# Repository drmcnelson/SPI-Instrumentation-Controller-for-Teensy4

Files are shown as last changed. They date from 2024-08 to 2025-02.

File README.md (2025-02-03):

# SPI Instrumentation Controller using Teensy 4.0

<p align="center">
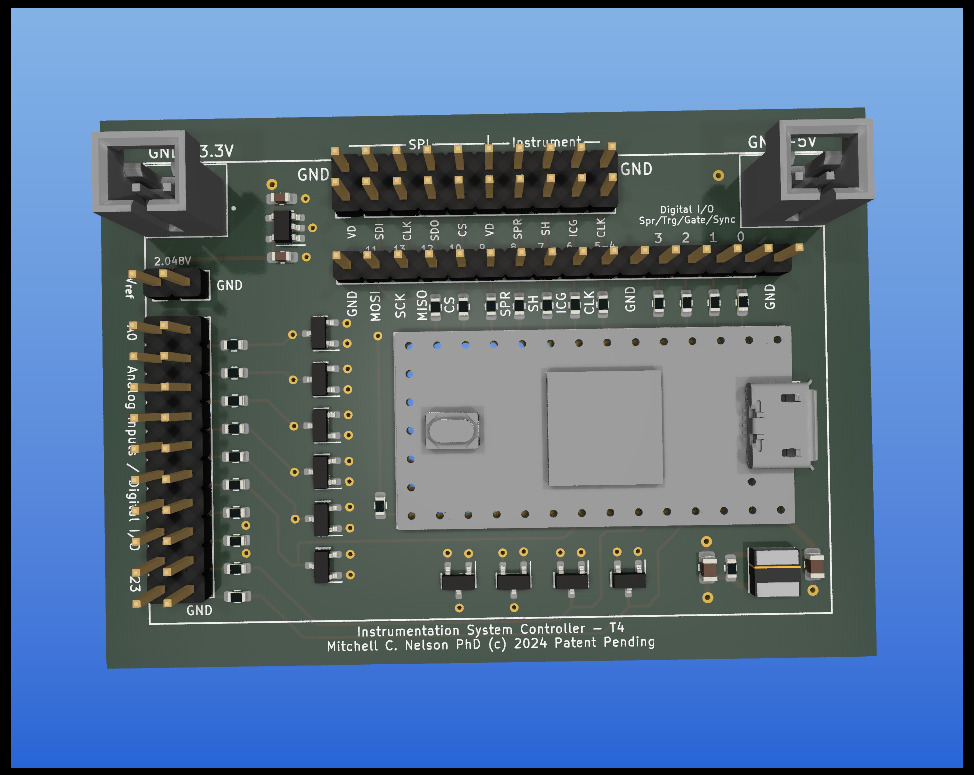
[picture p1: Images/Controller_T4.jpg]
Controller_T4

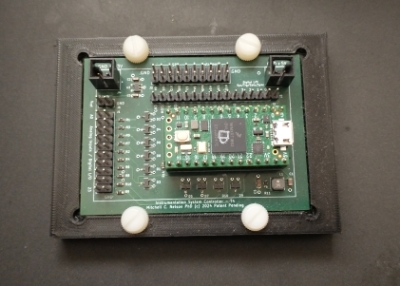
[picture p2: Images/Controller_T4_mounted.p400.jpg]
Controller_T4

</p>

Controller board for the SPI Instrumentation project, hosts a Teensy 4.0 and provides connectors for SPI, instrumentation control, 3.3V and 5V power, a precision voltage references, dedicated pins for trigger and gate input, sync and busy output and a set of pins that can be used for analog input or digital i/o.   The connectors are identified in images below.

## Connectors

The following shows the location of the pins for the SPI interface circled in red.

<p align="center">
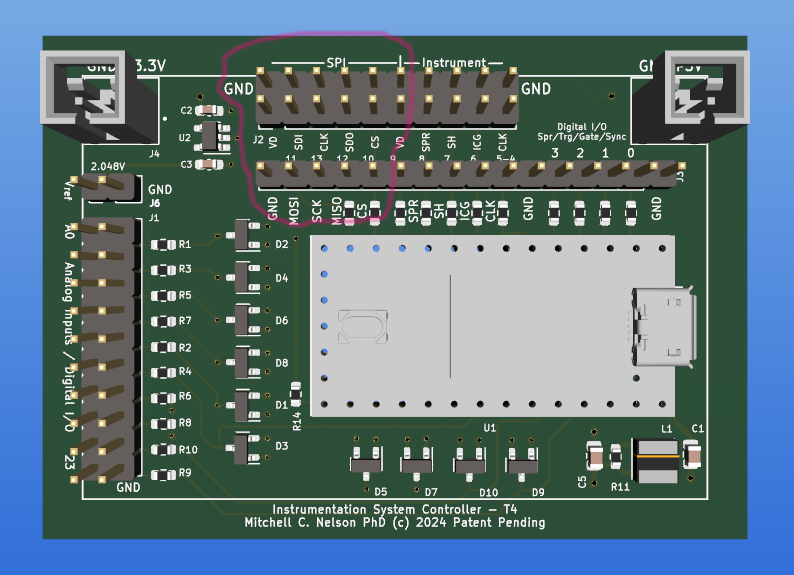
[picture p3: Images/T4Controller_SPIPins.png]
Controller_T4_SPI

</p>

The following shows the location of the pins for interfacing to the Linear CCD SPI boards, circled in red.

<p align="center">
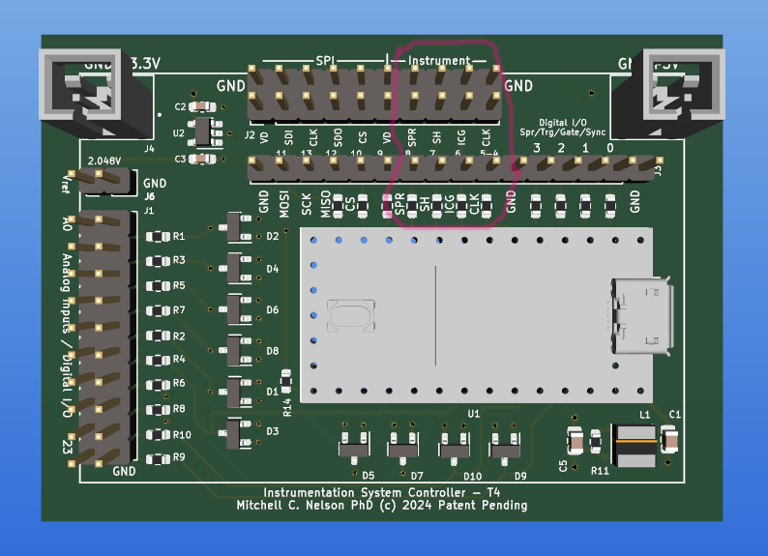
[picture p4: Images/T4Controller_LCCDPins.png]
Controller_T4_LCCD

</p>

The following shows the location of the pins for trigger and gate input and sync and busy output, circled in red.

<p align="center">
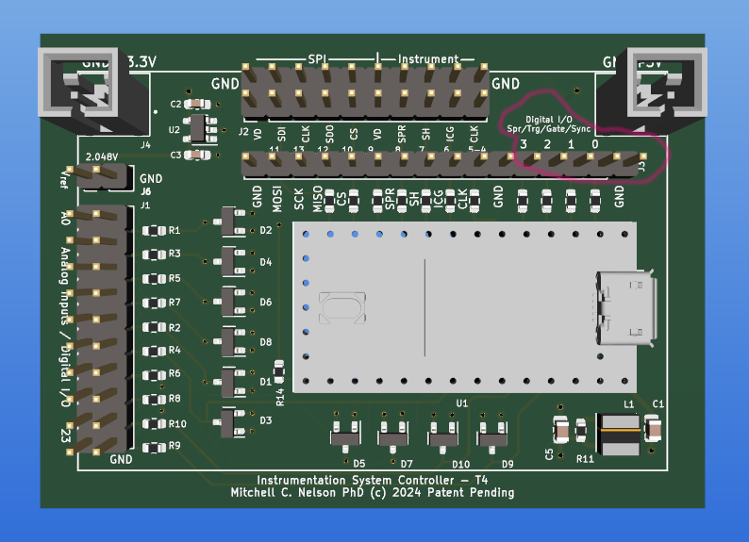
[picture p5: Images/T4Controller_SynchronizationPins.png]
Controller_T4_LCCD

</p>

## Example use
Here is an example of how the board is used, the other two boards in this picture are the InAmp and +5V,-5V power supply.

<p align="center">
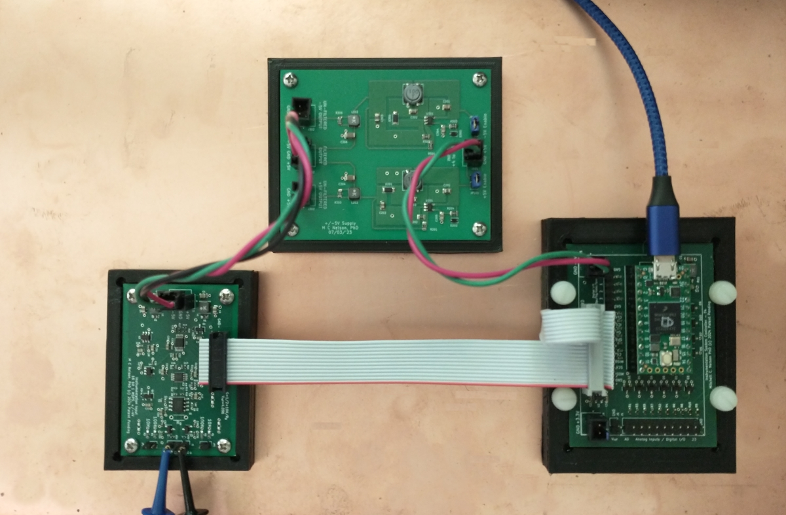
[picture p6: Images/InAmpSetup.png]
Controller_setup

</p>

## Obtaining boards

This repo includes files for FAB and assembly. 

You can [order assembled boards from PCBWAY here](https://www.pcbway.com/project/shareproject/Controller_Teensy_4_0_for_SPI_Instrumentation_boards_4b27edb1.html).

To assemble the board yourself you will need a reflow oven.  You can order bare boards from a sevice such as PCBWay or AllPCB, and use the BOM spreadsheet file to order parts from Digikey

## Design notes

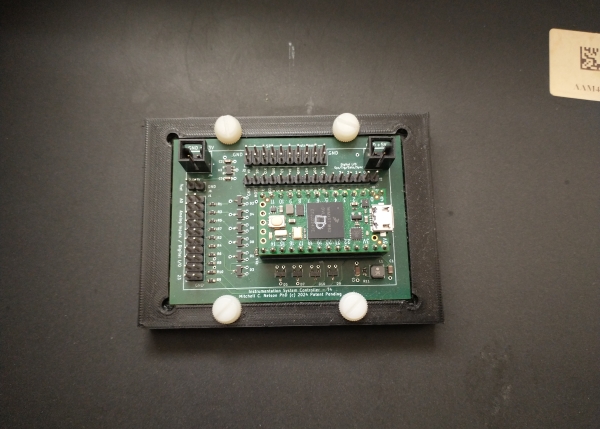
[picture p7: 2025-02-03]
Images/Controller_T4_mounted.jpg

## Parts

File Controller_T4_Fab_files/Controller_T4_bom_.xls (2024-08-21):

SMT Components | References | Value | Description | Footprint | Quantity Per PCB | Digikey
1 | C1 C5 | 22uF | CAP CER 22UF 25V X5R | C_0805_2012Metric | 2 | 490-12389-1-ND
2 | C2 | 10uF | Cap Cer 10uf 16V X5R | C_0603_1608Metric | 1 | 490-12317-1-ND
3 | C3 | 1uF | Cap Cer 1uf 16V X5R | C_0603_1608Metric | 1 | 1276-1034-1-ND
4 | D1-D10 | BAV99 | DIODE ARR GP 100V 215MA TO236AB | SOT-23 | 10 | 1727-2914-1-ND
5 | L1 | 10uH | FIXED IND 10UH 1.2A 180 MOHM SMD | L_Taiyo-Yuden_NR-40xx | 1 | 587-2886-1-ND
6 | R12-R23 | 49.9 | RES 49.9 OHM 1% 1/10W 0603 | R_0603_1608Metric | 12 | RMCF0603FT49R9CT-ND
7 | R1-R11 | 100R | RES 100 OHM 1% 1/4W 0603 | R_0603_1608Metric | 11 | 10-ERJ-UP3F1000VCT-ND
8 | U2 | LM4132xMF-2.0 | Fixed Ref 2.048V in SOT-23-5 | Package_TO_SOT_SMD:SOT-23-5 | 1 | LM4132BMF-2.0/NOPBCT-ND
 |  |  |  | Total SMT components | 39
Thru-Hole Parts
9 | J4-J5 |  | CONN HEADER VERT 2POS 2.54MM | MOLEX_705430001 | 2 | WM4800-ND
10 | J6 |  | CONN HEADER VERT 2POS 2.54MM | PinHeader_1x02_P2.54mm_Vertical | 1 | 3M156268-02-ND
11 | J3 | Conn_01x16_Male | CONN HEADER VERT 16POS 2.54MM | PinHeader_1x16_P2.54mm_Vertical | 1 | 3M156268-16-ND
12 | J1-J2 | Conn_02x10_Odd_Even | CONN HEADER VERT 20POS 2.54MM | PinHeader_2x10_P2.54mm_Vertical | 2 | 3M156308-20-ND
 |  |  |  | Total Thru-hole Components | 6
Teensy 4.0
DNP | Teensy (U1) | Teensy4.0 | Teensy4.0 | Teensy40 (2rows 0.6”, 14pins 0.1”, aligns with dip 28 W15.24) | 1 | 1568-DEV-16997-ND
DNP | Headers (U1) |  | Thru hole Headers, as socket for the Teensy4 |  | 2 | S7047-ND
DNP | Pins (U1) |  | Mating pins for the headers |  | 2 | 929647-01-14-EU
Accessories
DNP |  |  | Ribbon Cable |  | 1 | 3M157973-1-ND
DNP |  |  | Ribbon Cable IDC Free Hanging End |  | 2 | MKC20A-ND
DNP |  |  | Mating 2-pin connector |  | 2 | WM2900-ND
DNP |  |  | Crimp Pins 22-24awg, gold |  | 4 | WM2512-ND

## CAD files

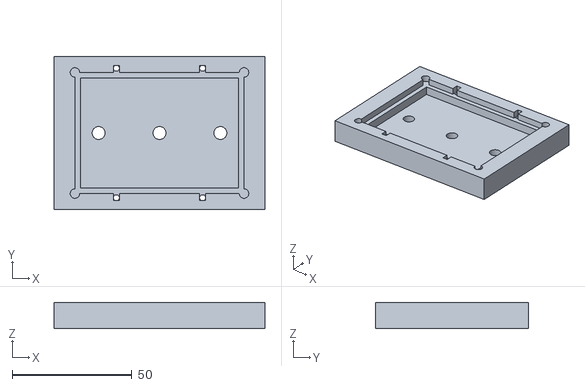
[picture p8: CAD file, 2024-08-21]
Base_3D_Printer_files/Controller_T4_base-Controller_T4_base.stl
88.0 x 64.0 x 11.0

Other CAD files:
Base_3D_Printer_files/Controller_T4_base.FCStd

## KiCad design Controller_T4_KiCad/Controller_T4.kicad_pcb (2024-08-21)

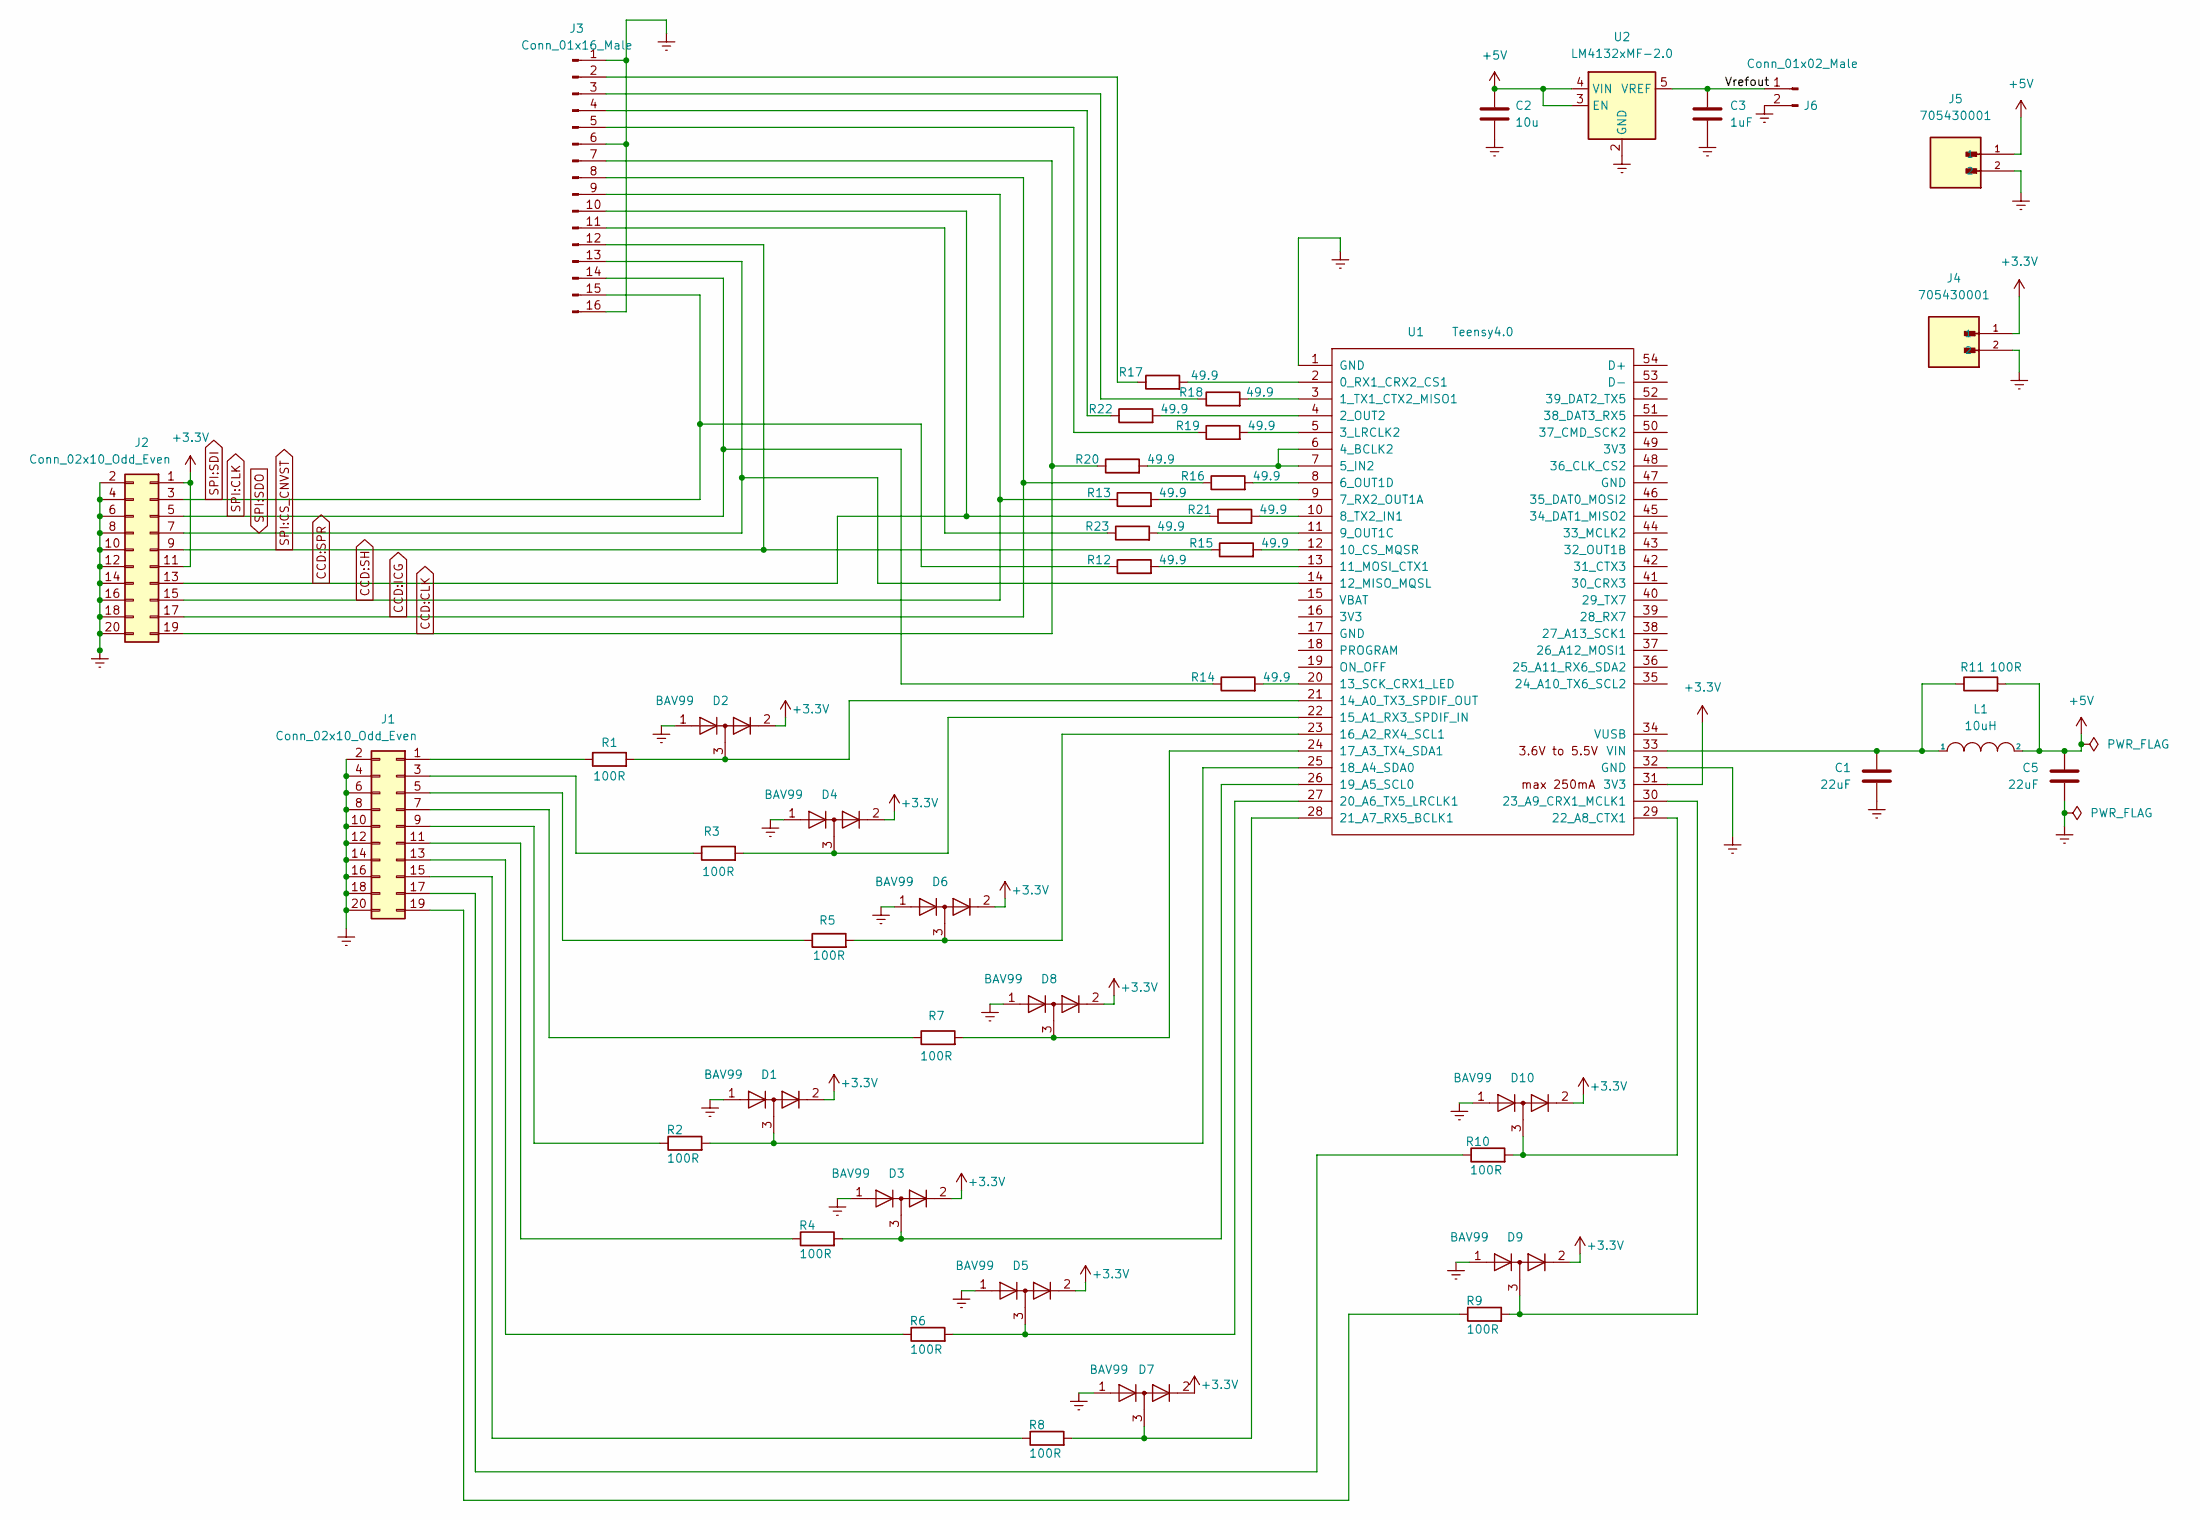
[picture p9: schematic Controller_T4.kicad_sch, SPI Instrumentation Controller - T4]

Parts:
C1, C5: 22uF; C_0805_2012Metric; Digikey 490-12389-1-ND
C2: 10u; C_0603_1608Metric_Pad1.08x0.95mm_HandSolder; Digikey 490-12317-1-ND
C3: 1uF; C_0603_1608Metric_Pad1.08x0.95mm_HandSolder; Digikey 1276-1034-1-ND
D1, D2, D3, D4, D5, D6, D7, D8, D9, D10: BAV99; SOT-23; Digikey 1727-2914-1-ND
J1, J2: Conn_02x10_Odd_Even; PinHeader_2x10_P2.54mm_Vertical; Digikey 3M156308-20-ND
J3: Conn_01x16_Male; PinHeader_1x16_P2.54mm_Vertical; Digikey 3M156268-16-ND
J4, J5: 705430001; MOLEX_705430001; PARTREV M1; Digikey WM4800-ND
J6: Conn_01x02_Male; PinHeader_1x02_P2.54mm_Vertical; Digikey 3M156268-02-ND
L1: 10uH; L_Taiyo-Yuden_NR-40xx; Digikey 587-2886-1-ND
R1, R2, R3, R4, R5, R6, R7, R8, R9, R10, R11: 100R; R_0603_1608Metric; Digikey 10-ERJ-UP3F1000VCT-ND
R12, R13, R14, R15, R16, R17, R18, R19, R20, R21, R22, R23: 49.9; R_0603_1608Metric; Digikey RMCF0603FT49R9CT-ND
U1: Teensy4.0; Teensy40; Digikey 1568-DEV-16997-ND
U2: LM4132xMF-2.0; SOT-23-5; Digikey LM4132BMF-2.0/NOPBCT-ND

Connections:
+3.3V: D1.2 (A), D2.2 (A), D3.2 (A), D4.2 (A), D5.2 (A), D6.2 (A), D7.2 (A), D8.2 (A), D9.2 (A), D10.2 (A), J2.1, J2.11, J4.1, U1.31 (3V3)
+5V: C2.1, C5.1, J5.1, L1.2, R11.2, U2.3 (EN), U2.4 (VIN)
/Vrefout: C3.1, J6.1, U2.5 (VREF)
CCD:CLK: J2.19, J3.7, R20.1
CCD:ICG: J2.17, J3.8, R16.1
CCD:SH: J2.15, J3.9, R13.1
CCD:SPR: J2.13, J3.10, R21.1
Earth: C1.2, C2.2, C3.2, C5.2, D1.1 (K), D2.1 (K), D3.1 (K), D4.1 (K), D5.1 (K), D6.1 (K), D7.1 (K), D8.1 (K), D9.1 (K), D10.1 (K), J1.2, J1.4, J1.6, J1.8, J1.10, J1.12, J1.14, J1.16, J1.18, J1.20, J2.2, J2.4, J2.6, J2.8, J2.10, J2.12, J2.14, J2.16, J2.18, J2.20, J3.1, J3.6, J3.16, J4.2, J5.2, J6.2, U1.1 (GND), U1.32 (GND), U2.2 (GND)
unnamed: C1.1, L1.1, R11.1, U1.33 (VIN)
unnamed: D1.3 (K), R2.2, U1.25 (18_A4_SDA0)
unnamed: D2.3 (K), R1.2, U1.21 (14_A0_TX3_SPDIF_OUT)
unnamed: D3.3 (K), R4.2, U1.26 (19_A5_SCL0)
unnamed: D4.3 (K), R3.2, U1.22 (15_A1_RX3_SPDIF_IN)
unnamed: D5.3 (K), R6.2, U1.27 (20_A6_TX5_LRCLK1)
unnamed: D6.3 (K), R5.2, U1.23 (16_A2_RX4_SCL1)
unnamed: D7.3 (K), R8.2, U1.28 (21_A7_RX5_BCLK1)
unnamed: D8.3 (K), R7.2, U1.24 (17_A3_TX4_SDA1)
unnamed: D9.3 (K), R9.2, U1.30 (23_A9_CRX1_MCLK1)
unnamed: D10.3 (K), R10.2, U1.29 (22_A8_CTX1)
unnamed: J1.1, R1.1
unnamed: J1.3, R3.1
unnamed: J1.5, R5.1
unnamed: J1.7, R7.1
unnamed: J1.9, R2.1
unnamed: J1.11, R4.1
unnamed: J1.13, R6.1
unnamed: J1.15, R8.1
unnamed: J1.17, R10.1
unnamed: J1.19, R9.1
unnamed: J3.2, R17.1
unnamed: J3.3, R18.1
unnamed: J3.4, R22.1
unnamed: J3.5, R19.1
unnamed: J3.11, R23.1
unnamed: R12.2, U1.13 (11_MOSI_CTX1)
unnamed: R13.2, U1.9 (7_RX2_OUT1A)
unnamed: R14.2, U1.20 (13_SCK_CRX1_LED)
unnamed: R15.2, U1.12 (10_CS_MQSR)
unnamed: R16.2, U1.8 (6_OUT1D)
unnamed: R17.2, U1.2 (0_RX1_CRX2_CS1)
unnamed: R18.2, U1.3 (1_TX1_CTX2_MISO1)
unnamed: R19.2, U1.5 (3_LRCLK2)
unnamed: R20.2, U1.6 (4_BCLK2), U1.7 (5_IN2)
unnamed: R21.2, U1.10 (8_TX2_IN1)
unnamed: R22.2, U1.4 (2_OUT2)
unnamed: R23.2, U1.11 (9_OUT1C)
SPI:CLK: J2.5, J3.14, R14.1
SPI:CS_CNVST: J2.9, J3.12, R15.1
SPI:SDI: J2.3, J3.15, R12.1
SPI:SDO: J2.7, J3.13, U1.14 (12_MISO_MQSL)

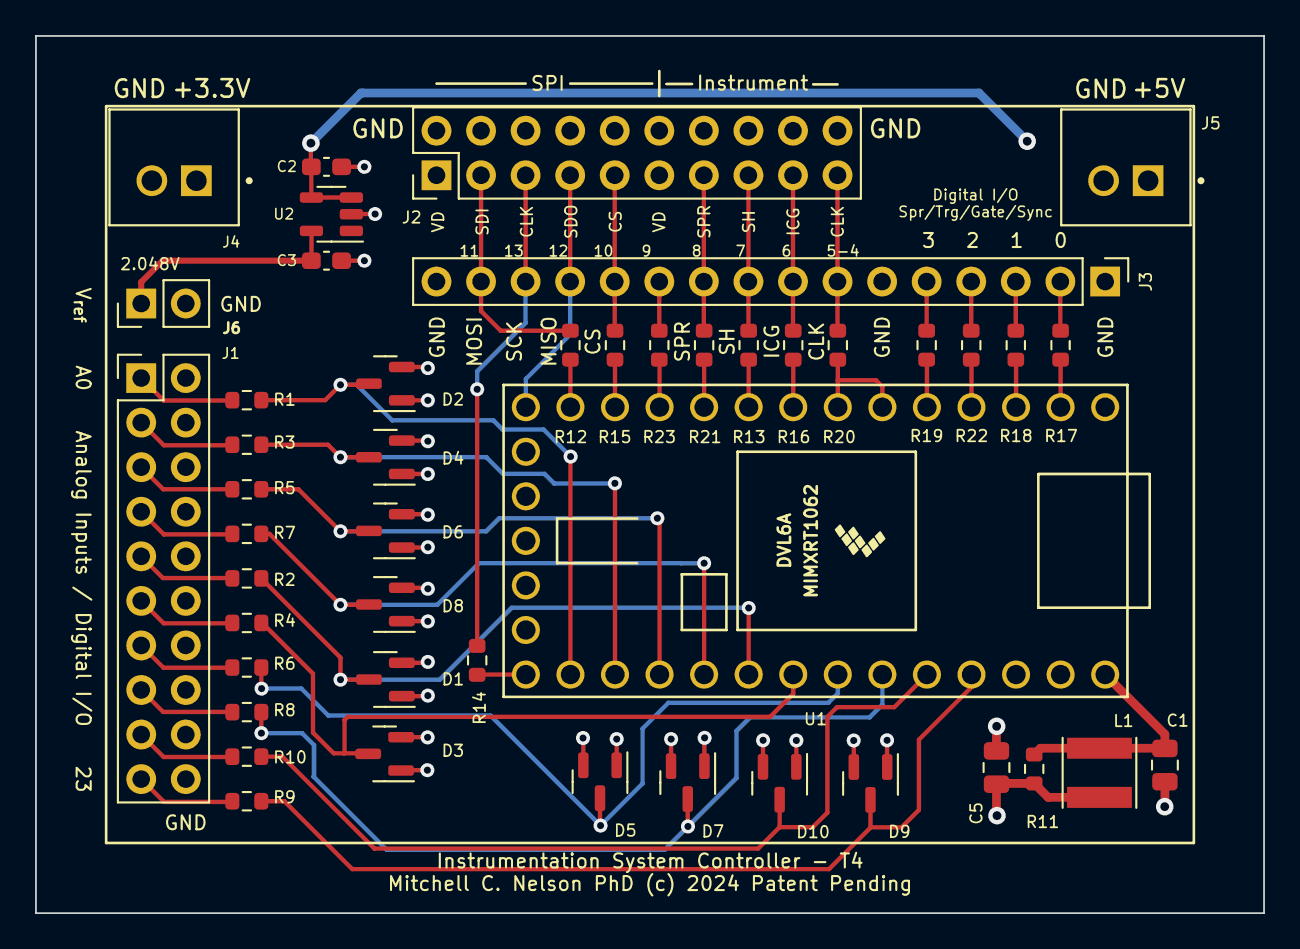
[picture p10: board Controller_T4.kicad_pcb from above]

Board: 4 copper layers, 70.0 x 50.0 mm, 46 parts (0 on the bottom side), 50 nets.

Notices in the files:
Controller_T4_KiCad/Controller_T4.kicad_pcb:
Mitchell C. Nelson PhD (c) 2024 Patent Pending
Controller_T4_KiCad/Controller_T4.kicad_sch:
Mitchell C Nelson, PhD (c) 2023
